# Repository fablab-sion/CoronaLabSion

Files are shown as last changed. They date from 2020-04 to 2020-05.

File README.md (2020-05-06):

# CoronaLabSion
Dépôt des actions menées durant la crise du Covid19.

Sous l'impulsion de Grégoire Largey et Lucas Monachon, le FabLab Sion et TheArk se sont alliés afin de lancer un appel aux makers de Sion et région afin de fournir du matériel à l'Hôpital de Sion. Le modèle "3DVerkstan" a été retenu à l'Hôpital car plus aisé à mettre et enlever rapidement. 

Pour toutes questions, vous pouvez contacter le FabLab Sion.

# Situation de la pandémie
Situation mondiale: https://gisanddata.maps.arcgis.com/apps/opsdashboard/index.html#/bda7594740fd40299423467b48e9ecf6

Situation en Suisse: [COVID-19_Situation_epidemiologique_en_Suisse.pdf](COVID-19_Situation_epidemiologique_en_Suisse.pdf)

# Visières faciales

## Modèle NewShield Shark
Testée par Lucas Monachon, ce modèle a la particularité qu'aucun trou n'est nécessaire pour accrocher la feuille plastique sur la monture. Un système ingénieux de clip à dents tient la feuille. Design développé par Julien Delnatte (CTO de http://mango.io), Marc Demange, Guillaume Raineri et Mathieu Saulenc. https://newshield.org

- Licence: https://creativecommons.org/licenses/by-nc-nd/2.0/fr/

- Monture:
	- Fichier STL "Monture" (unité: mm): [newshield-shark-notext.stl](newshield-shark-notext.stl)
	- Fichier STL "Boucles" : vous devez imprimer une paire de boucle en fonction de l'épaisseur de vôtre élastique. 
	- Matière: PLA
	- Quantité utilisée: environ 20g 
	- Précision: 0.39mm est suffisant (sur une Zortrax M200)
	- Infill: 0% ou 10% pas plus.
	- Temps d'impression: environ 1h30 (sur une Zortrax M200)
	
- Visière:
	- Pour la visière, utiliser une feuille A4 transparente de 0.2mm d'épaisseur, éventuellement de 0.15mm.
	- Ces visières vont tout simplement venir se cliper dans la monture.
	
- Assemblage:
	- voir notice : [notice-newshield-shark-livret.pdf](notice-newshield-shark-livret.pdf)

## Modèle 3DVerkstan
Testée par Grégoire Largey, ce modèle est fait pour être utilisée avec une feuille trouée au moyen d'une perforatrice 2 trous qui est commune dans toute l'Europe. Design développé par https://3dverkstan.se/protective-visor/.

- Licence: https://creativecommons.org/licenses/by-sa/3.0/deed.fr

- Monture:
	- Fichier stl (unité: mm): [Visor_frame_EUROPE_80mm_4hole_v1-Batch_test-single.stl](Visor_frame_EUROPE_80mm_4hole_v1-Batch_test-single.stl)
	- Matière: PLA
	- Quantité utilisée: environ 11-12g 
	- Precision: 0.2mm est suffisant (sur une Prusa i3 Mk3s)
	- Infill: 15% est suffisant (Veillez à ne pas trop remplir pour garder la souplesse)
	- Temps d'impression: environ 1h (sur une Prusa i3 Mk3s)
	
- Visière:
	- Cette visière doit être découpée dans une feuille A4 transparente de 0.15mm d'épaisseur, au maximum dans du 0.18mm.
	- Si la matière est du PVC, faire les trous à l'aide d'une perforatrice standard :

		1. Réglez votre perforatrice sur la position d'une feuille A6, en tirant sur la barre de guidage jusqu'à ce qu'elle indique "A6".
		2. Faites un test de perforation sur un morceau de papier, puis mesurez la distance entre les trous et chaque bord et assurez-vous que la perforation est symétrique.
		3. Faites une perforation sur un côté du côté long de la feuille A4

		4. Retournez la feuille A4 autour de son axe court, et faites une perforation sur le côté opposé, de façon à obtenir 4 trous sur le même bord.
		
	- Si la matière est du PET, la feuille peut être découpée au moyen d'une découpeuse laser selon le template ci-dessus.

- Assemblage: La feuille vient se cliper sur les ergots.

## Modèle "Minimalist"
Un test de ce modèle (https://hackaday.io/project/170481-laser-cut-medical-shield) sera réalisé au FabLab de Renens. C'est une visière conçue par Konrad Klepacki et Mateusz Dyrda et qui présente l'avantage d'être produite uniquement par découpage de feuilles de PETG de 0.5 mm d'épaisseur.

# Extenseurs pour masques
Vous pouvez aussi trouver des extenseurs pour soulager la pression subie derrière les oreilles. Vous pouvez trouver un modèle mini et un modèle grand.

## Modèle "Newshield"
- STL grand modèle: [newshield-ear-protector-v2.stl](newshield-ear-protector-v2.stl)
- STL petit modèle: [newshield-ear-protector-mini-v2.stl](newshield-ear-protector-mini-v2.stl)

## Modèle "Surgical remix"
- Fichier STL: [Surgical_Mask_Strap_Remix.stl](Surgical_Mask_Strap_Remix.stl)

# Informations sur les matières
- Le PLA ou le PETG plus idéalement semblent être des matières adéquates pour la production des montures imprimées en 3D.
- Le PVC ou le PET plus idéalement peuvent convenir pour les visières qui pourraient être désinfectées mais finalement consommées rapidement.

Ce document fait état de plusieurs type de désinfectant et permet d'avoir une vue sur ce qui peut aller suivant la matière de la monture désinfectée. https://faceshield.us/wp-content/uploads/2020/04/Sanitizing_Instructions.pdf

# Paramètres d'impression
Attention aux quelques soucis de qualité d'impression, ces montures doivent rester un minimum confortables. Les paramètres d'impression jouent un rôle très important à ce niveau. Cette vidéo explique très bien les paramètres de base auxquels faire attention : [https://youtu.be/-7cbijYlGj4](https://youtu.be/-7cbijYlGj4)

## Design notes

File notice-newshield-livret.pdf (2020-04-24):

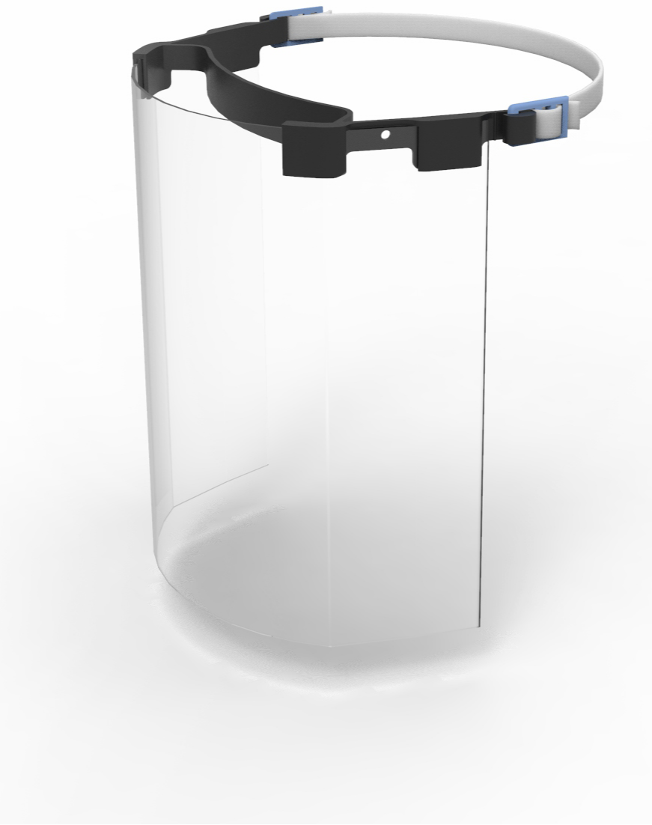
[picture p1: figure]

MERCI POUR TOUT, BON COURAGE.

Fichiers 3D, demandes de livraison, conseils,... : hp://www.newshield.org

# VISIERE DE PROTECTION NEWSHIELD

# - Notice -

### 1 : Avis importants

- visière imprimée en 3d
- maère PLA/PETG
- Cee visière n'est pas homologuée par les
organismes habilités
- Cee visière ne peut pas se substuer aux masques homologués ou autres équipements homologués
- cee visière n'est pas désinfectée, cela doit se faire avant la 1ère ulisaon

### 2 : Les différents éléments

Le support de tête | Aaches pour Élasque x2
“NewShield” | Les aaches peuvent différer en foncon des élasques.

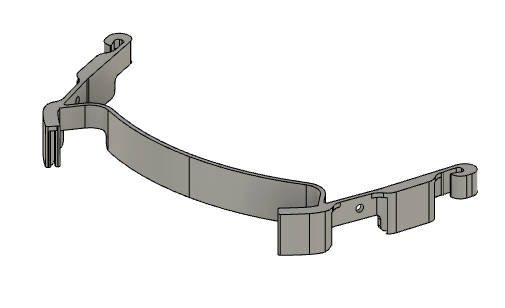
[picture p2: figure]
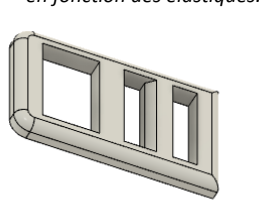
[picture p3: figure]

- 1 Feuille de PVC +- 200 microns format A4 (150 microns Mini)
- Élasque (à couper)

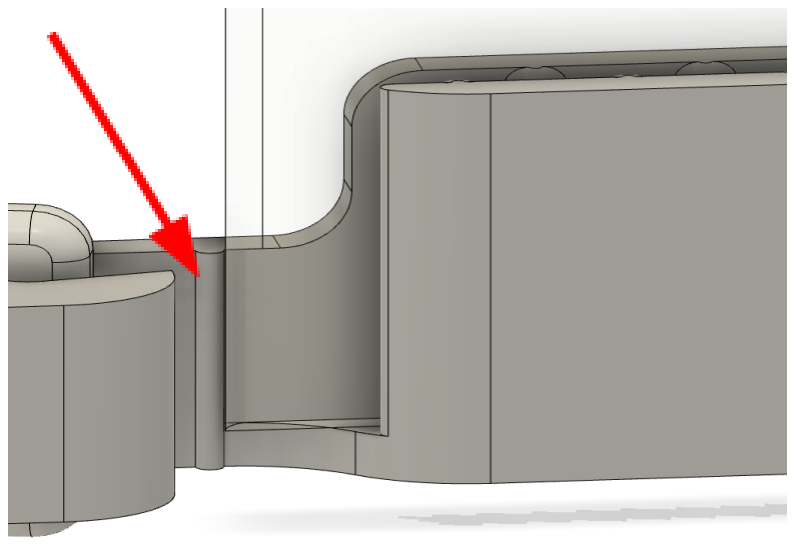
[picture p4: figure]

### 3 : Montage

1 : Coupez l’élasque pour en former une bande
2 : Enfilez l’élasque dans les « Aaches » à chaque extrémité suivant le schéma ci-joint

3 : Clipsez les aaches de chaque côté du support « NewShield »

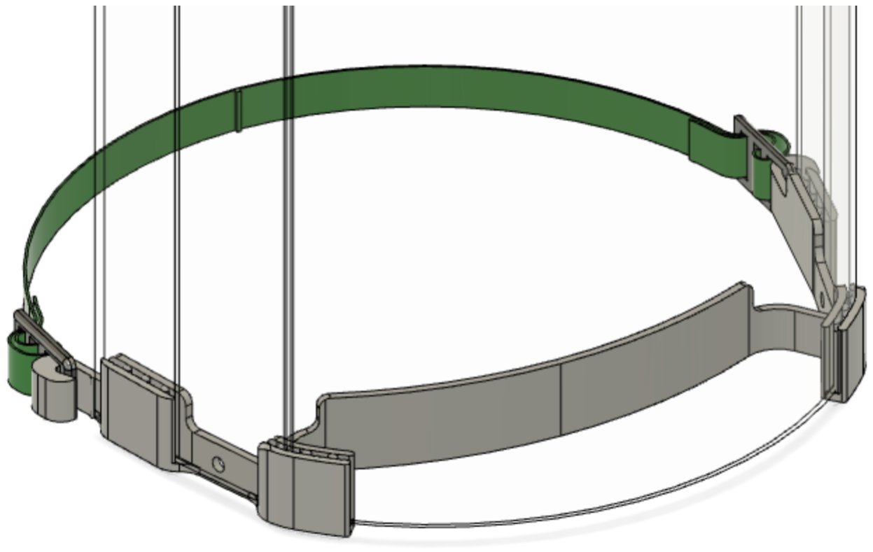
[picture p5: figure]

4 : Insérer la feuille PVC dans les 4 « Griffes » en la glissant en mode « Paysage » (la pare la plus large). Un détrompeur permet de vous guider sur la façon d’ajuster la feuille. La feuilles se pliera en accordéons pour améliorer la tenue.

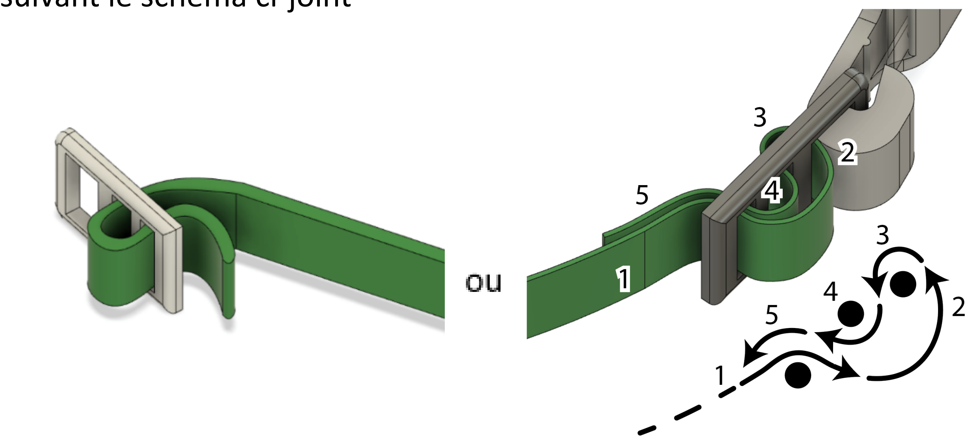
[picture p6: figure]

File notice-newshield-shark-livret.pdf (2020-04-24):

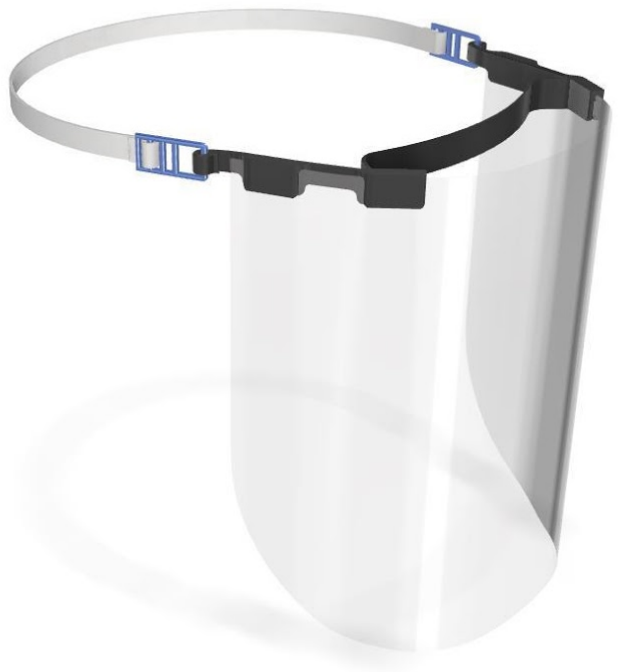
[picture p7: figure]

MERCI POUR TOUT, BON COURAGE.

Fichiers 3D, demandes de livraison, conseils,... : hp://www.newshield.org

# VISIERE DE PROTECTION NEWSHIELD SHARK

# - Notice -

### 1 : Avis importants

- visière imprimée en 3d
- maère PLA/PETG
- Cee visière n'est pas homologuée par les organismes habilités
- Cee visière ne peut pas se substuer aux masques homologués ou autres équipements homologués
- cee visière n'est pas désinfectée, cela doit se faire avant la 1ère ulisaon

### 2 : Les différents éléments

Le support de tête | Aaches pour Élasque x2
“NewShield Shark” | Les aaches peuvent différer en foncon des élasques.

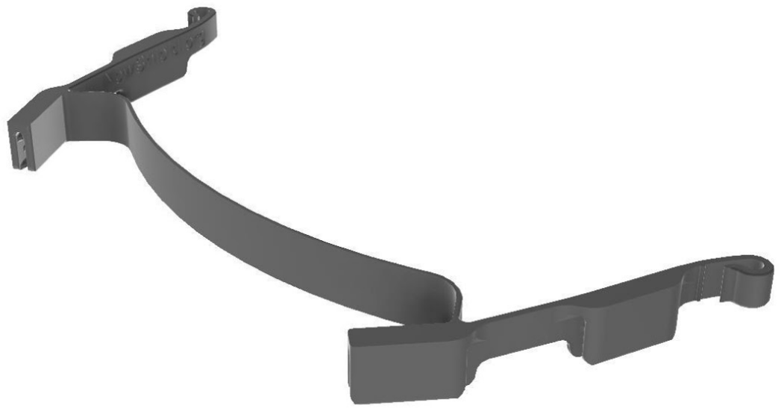
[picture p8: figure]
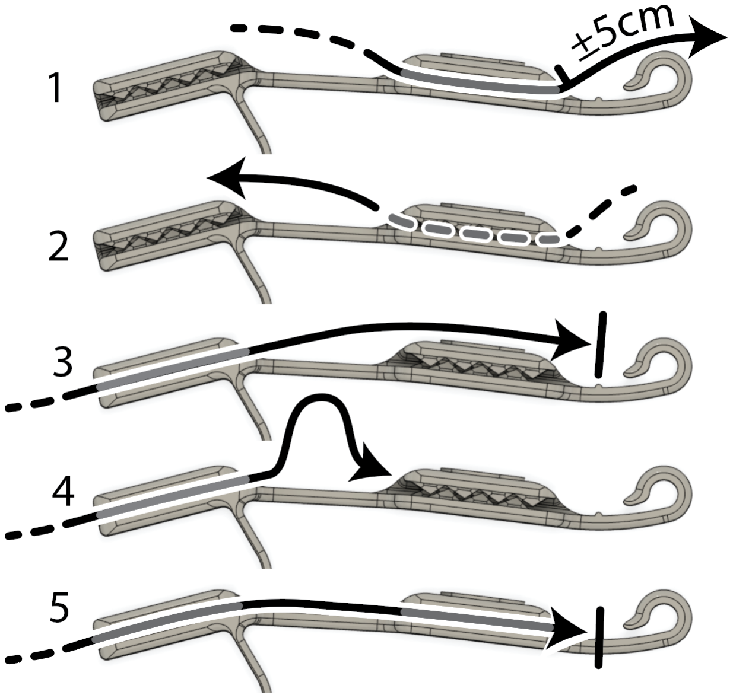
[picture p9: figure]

- 1 Feuille de PVC +- 200 microns format A4 (150 microns Mini)
- Élasque (à couper)

### 3 : Montage

1 : Coupez l’élasque pour en former une bande
2 : Enfilez l’élasque dans les « Aaches » à chaque extrémité suivant le schéma ci-joint

3 : Clipsez les aaches de chaque côté du support « NewShield Shark»

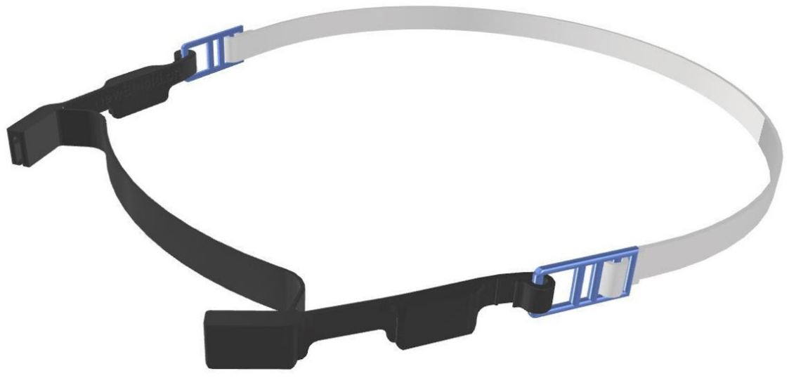
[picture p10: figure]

4 : Insérer la feuille PVC dans les 4 « Griffes » en la glissant en mode « Paysage » (la pare la plus large). Un détrompeur permet de vous guider sur la façon d’ajuster la feuille. La feuilles se pliera en accordéons pour améliorer la tenue.

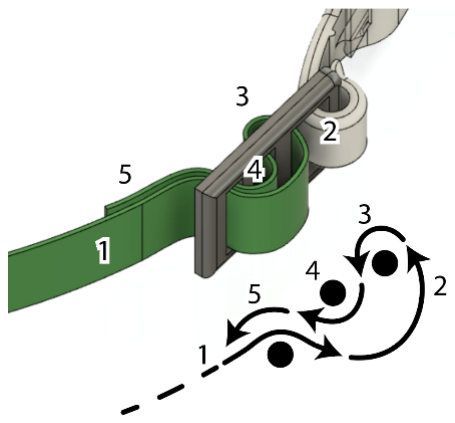
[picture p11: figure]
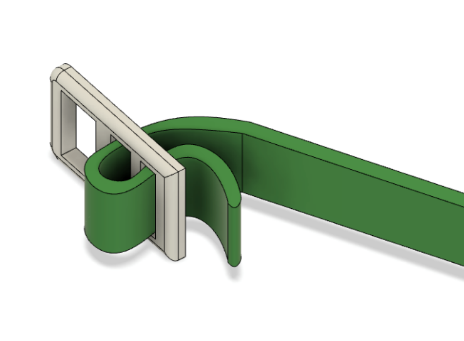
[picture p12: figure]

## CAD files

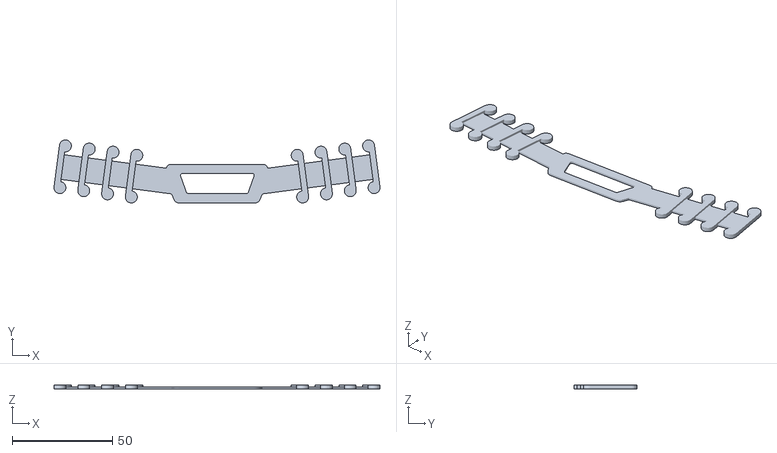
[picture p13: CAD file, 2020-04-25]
Surgical_Mask_Strap_Remix.stl
163.0 x 31.5 x 2.00

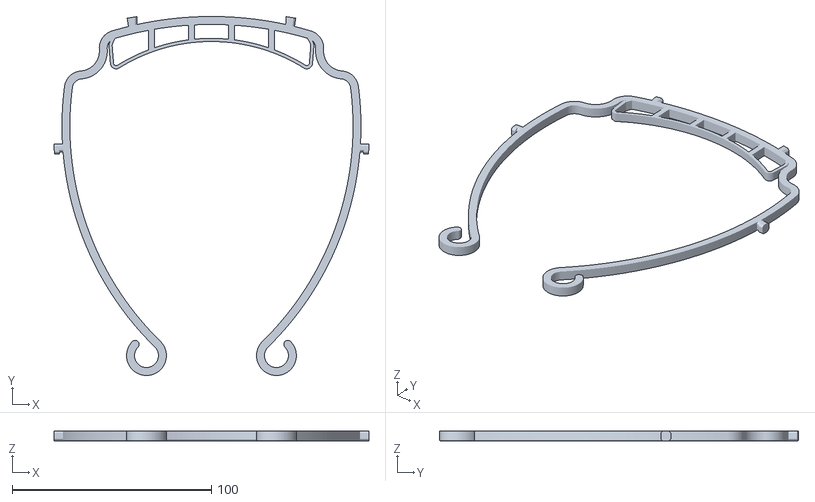
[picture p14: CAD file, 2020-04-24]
Visor_frame_EUROPE_80mm_4hole_v1-Batch_test-single.stl
157.8 x 180.1 x 5.00

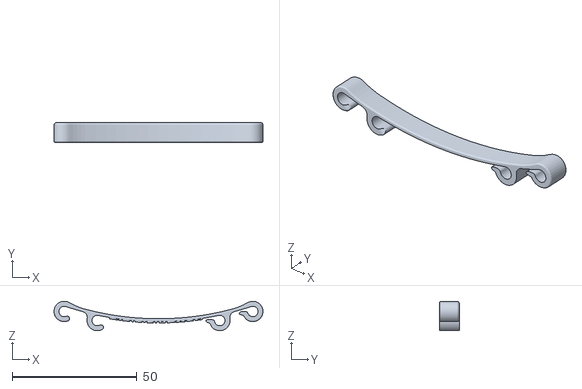
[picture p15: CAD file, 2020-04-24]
newshield-ear-protector-mini-v2.stl
83.9 x 8.00 x 11.8

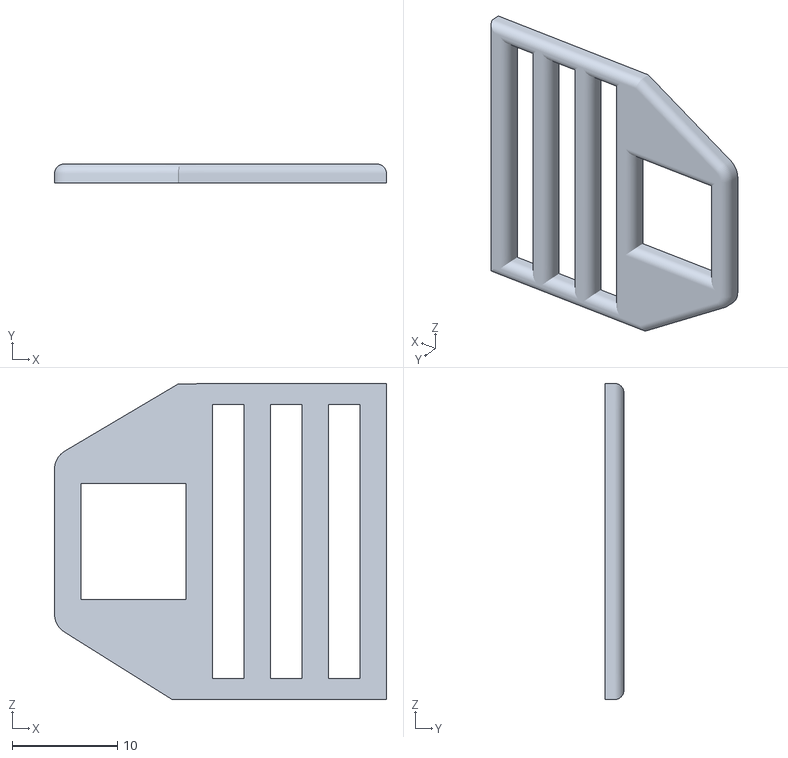
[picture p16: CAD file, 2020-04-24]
bouclev3-25mm.stl
31.5 x 1.80 x 30.0

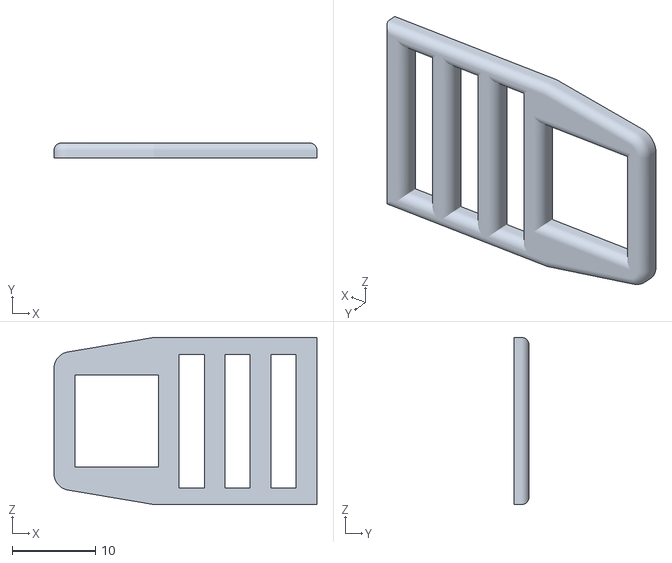
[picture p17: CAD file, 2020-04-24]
bouclev3-15mm.stl
31.5 x 1.80 x 20.0

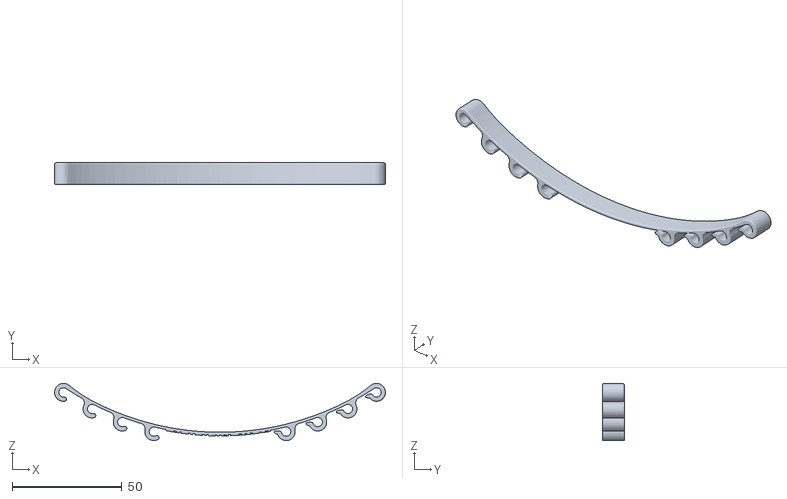
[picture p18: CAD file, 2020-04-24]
newshield-ear-protector-v2.stl
150.9 x 10.0 x 26.1

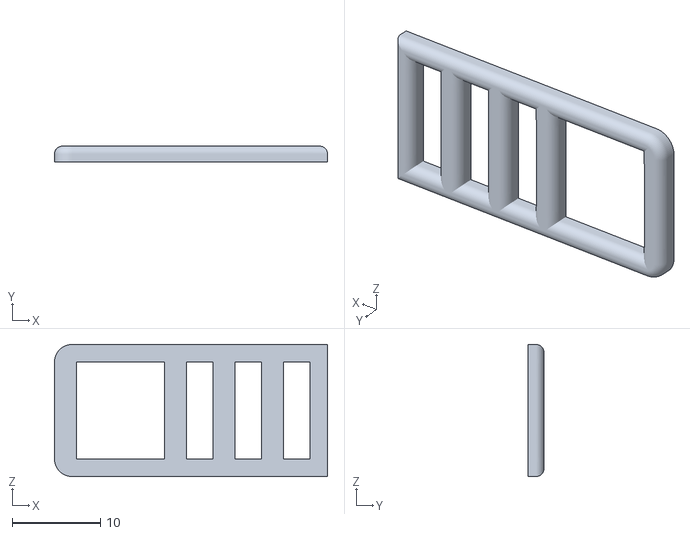
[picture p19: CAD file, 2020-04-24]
bouclev3-10mm.stl
31.0 x 1.80 x 15.0

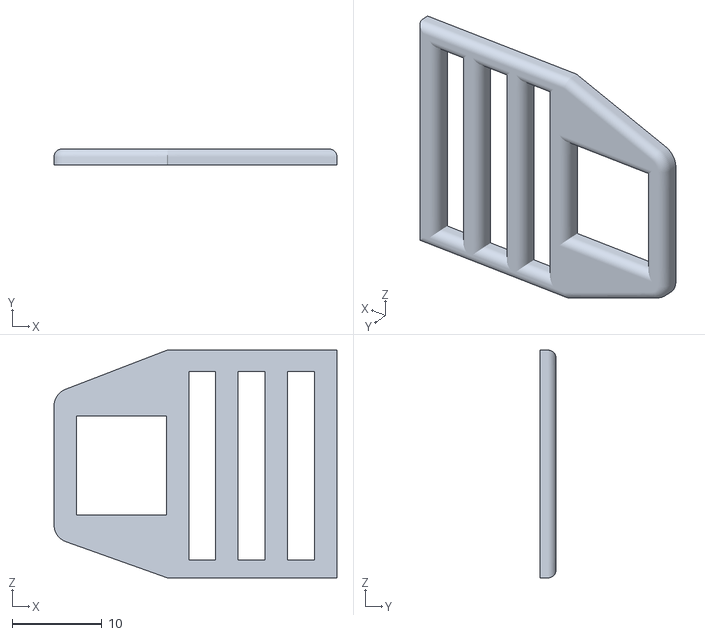
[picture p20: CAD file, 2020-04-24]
bouclev3-20mm.stl
31.5 x 1.80 x 25.4

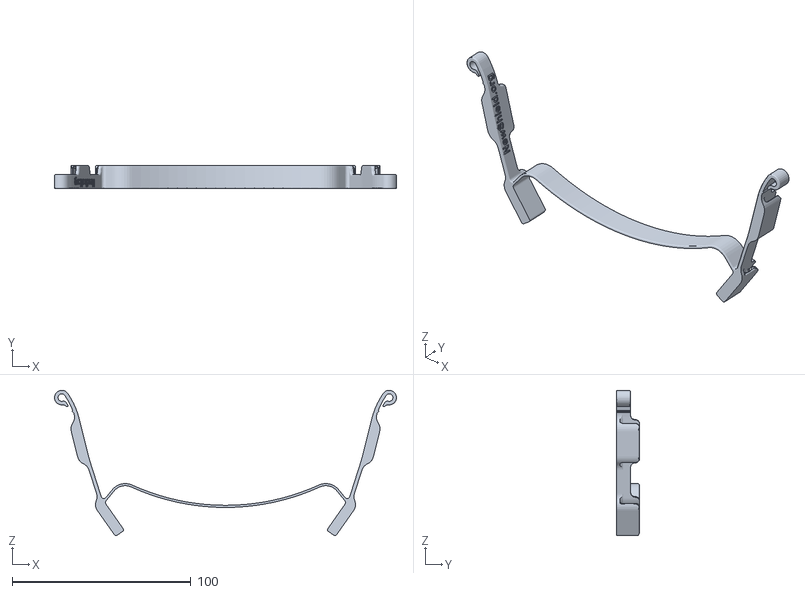
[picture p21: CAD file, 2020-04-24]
newshield-shark-notext.stl
191.6 x 13.0 x 81.4

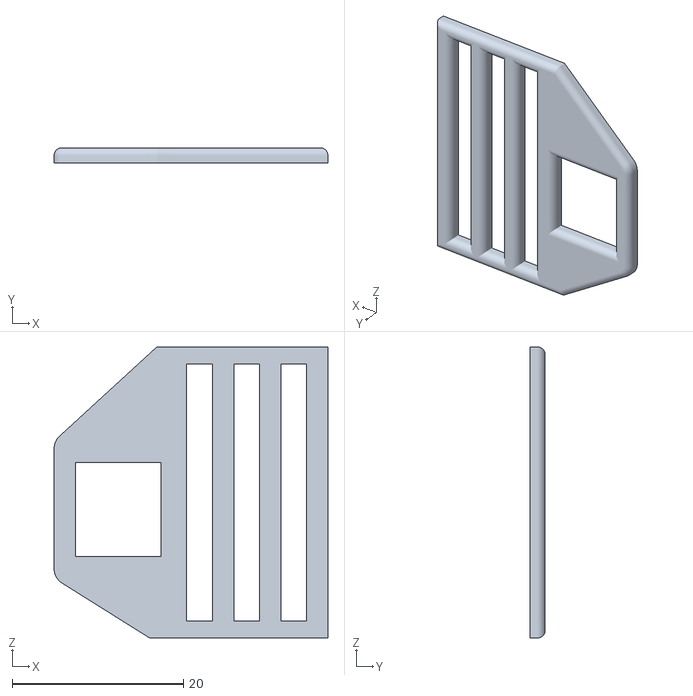
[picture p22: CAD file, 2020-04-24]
bouclev3-30mm.stl
32.0 x 1.80 x 34.0

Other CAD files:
newshield-shark-visiere-solidaire.stl
